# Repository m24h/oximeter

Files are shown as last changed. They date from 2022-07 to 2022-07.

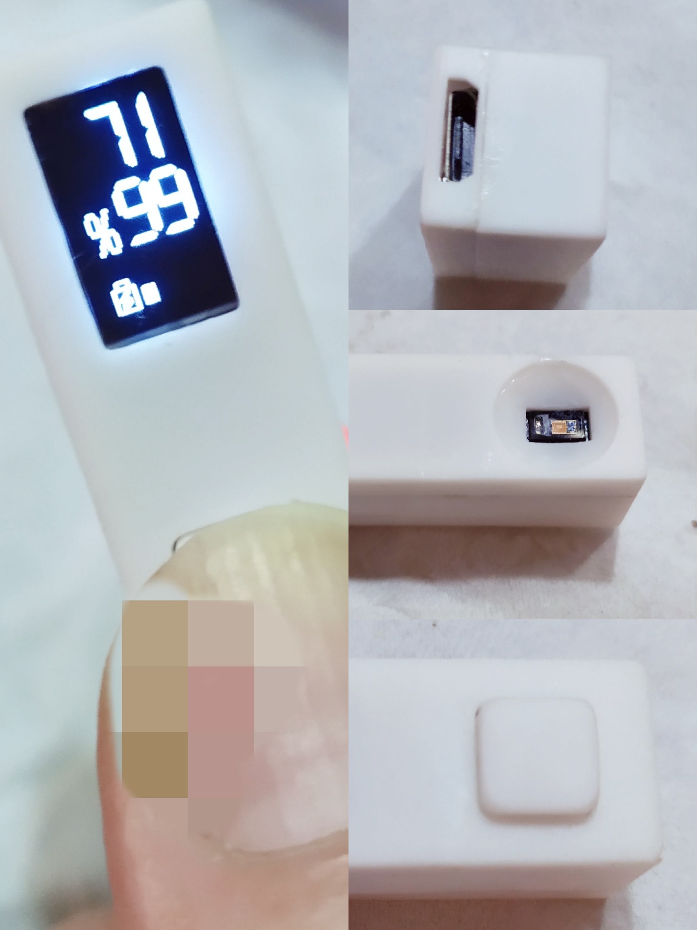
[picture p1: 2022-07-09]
running/usage.jpg

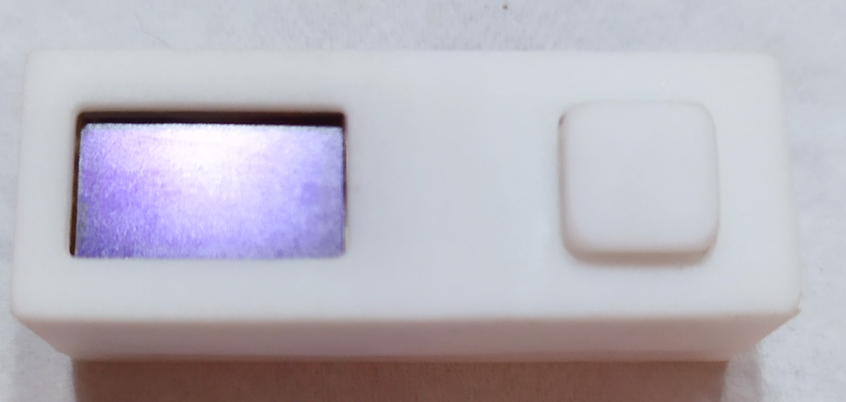
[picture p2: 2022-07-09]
running/top.jpg

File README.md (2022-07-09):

# oximeter
A small oximeter using MAX30102/STC8G1K08A/0.5-inch-OLED/Phase-Detect algorithm

features:

1. SpO2 detection.
2. Heart beat rate detection.
3. With a USB charging interface.
4. Small and cheap.
5. Compatible with Keil C51 or SDCC

!!!IMPORTANT!!!

First thing:
I made an ergonomic mistake in my design, my original idea was to use a button to turn on the power and the sensor underneath would just fit the finger.
But the excessive pressure affected the blood flowing in the finger, also the results.
I suggest that subsequent developers can modify the PCB and box case, use a toggle switche instead of the button, which can be placed on the side of the case, and place the sensor on the same side of the OLED (Top side), So the users can just touch the sensor surface gently by a finger, that would result in fast and accurate detection results.

Second thing:
Hex file for burning/Downloading is included here, TTL serial port is connected to D+/D- pin of USB charging interface, subsequent developers can also try to download hex file directly using pseudo USB downloading port of STC8G1K08A (ID pin of micro-USB port is required to be connected to GND, but I've never tried, and I heard that there is a certain failure rate).
But STC-ISP V6.90 (the STC official downloading software) has an strange BUG, which will cause straightforward downloading to fail.
In my design, I put const parameters like fonts and some tables into EEPROM area (which is indexed from 0x2000), STC-ISP says "This file is over the valid scope, and the exceeding part has been moved to EEPROM area", which looks as expected, BUT it is not. STC-ISP does not split the hex file at 0x2000, but at 0x1FF9.
The workaround for this strange problem is to manually delete first 7 bytes at "EEPROM Buffer" tab-page on the STC-ISP interface, and "Save Buffer" to a .bin file, and re-load the file using "Open EEPROM file", the burn it.

Other downloading things:
IRC frequency is 22.1184MHz.
Don't enable WDT.
Rest pin is used as I/O port.

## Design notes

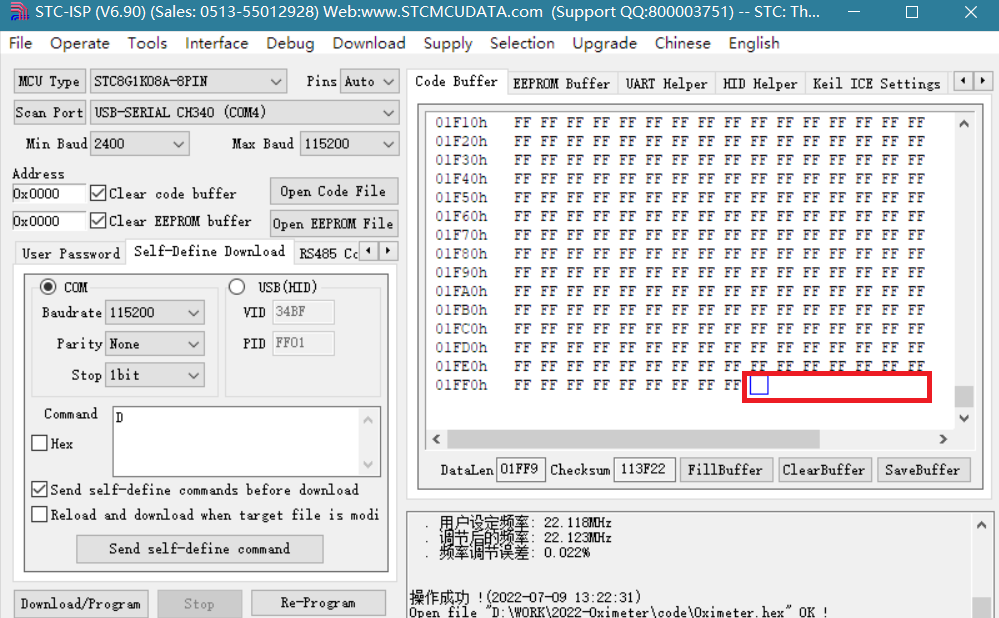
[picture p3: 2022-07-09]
running/stc-isp-wrong-splitting.png

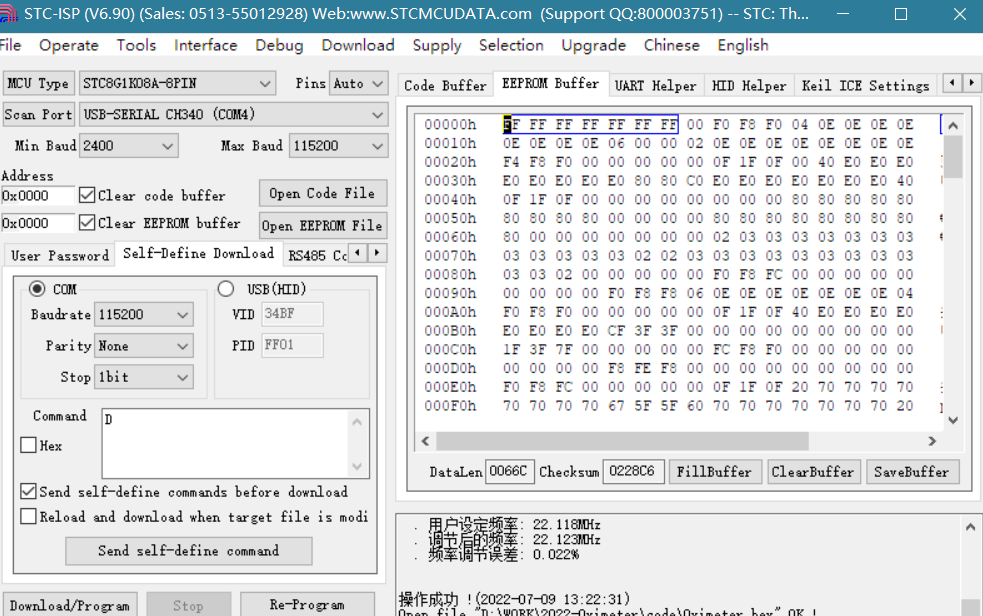
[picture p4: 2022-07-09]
running/stc-isp-must-delete-7bytes.png

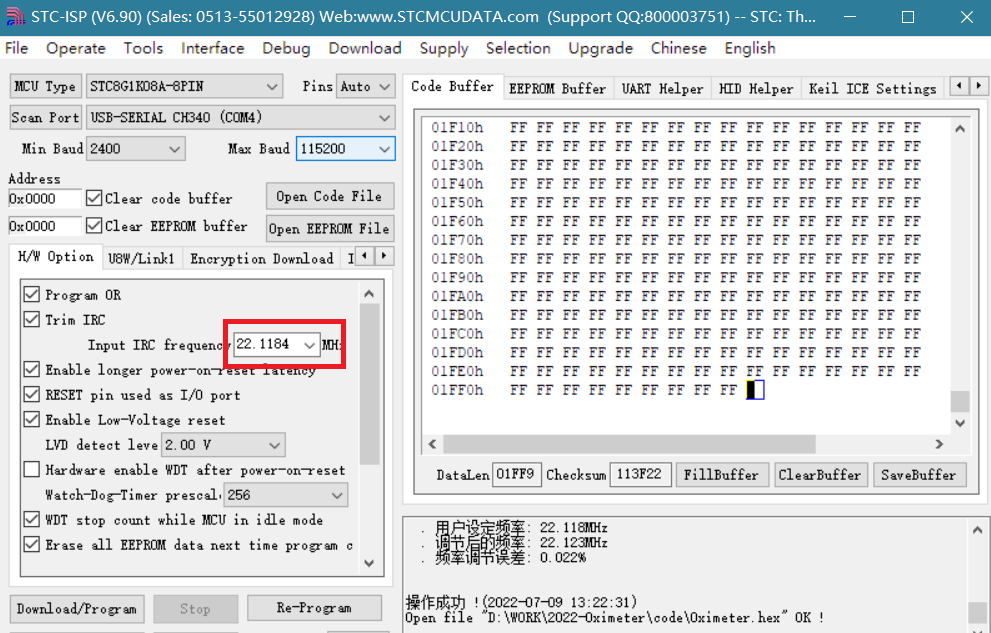
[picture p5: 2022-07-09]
running/stc-isp-freq.png

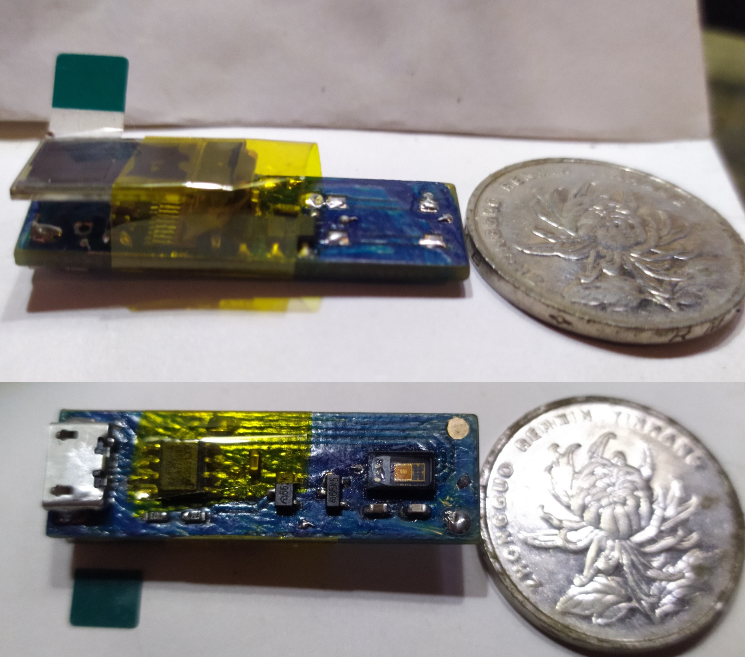
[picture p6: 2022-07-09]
running/pcb.jpg

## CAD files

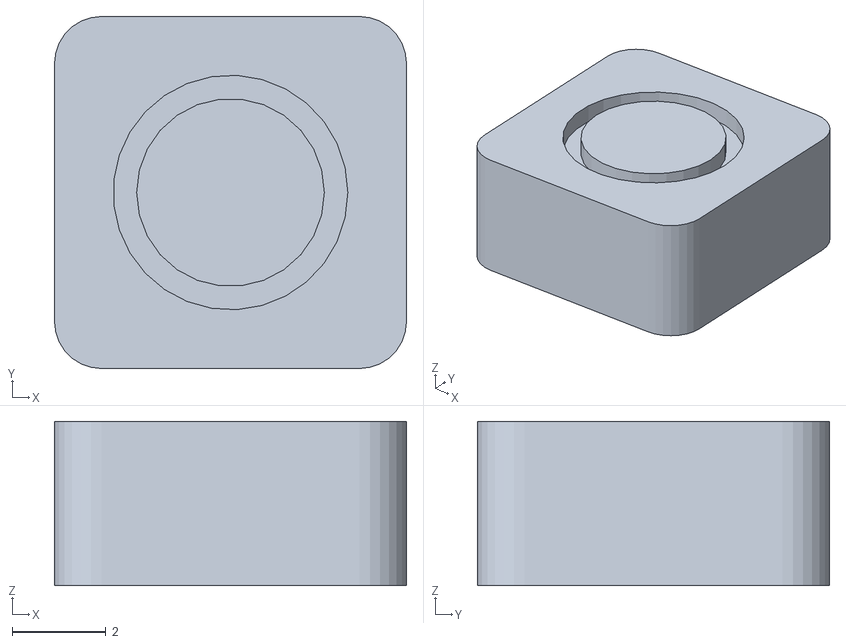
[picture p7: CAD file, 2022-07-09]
parts/button.stl
7.50 x 7.50 x 3.50

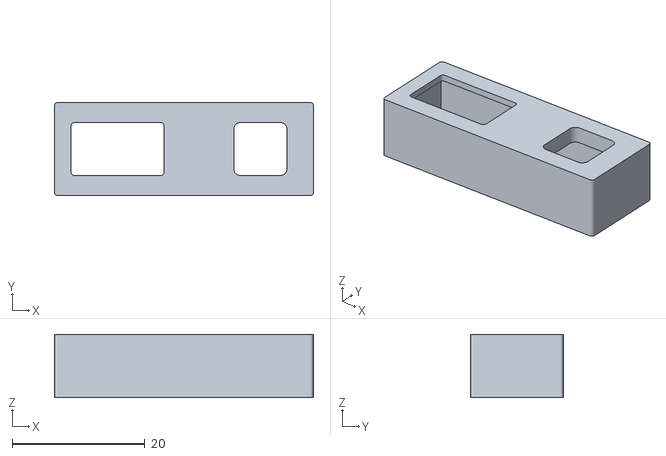
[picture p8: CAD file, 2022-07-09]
parts/top.stl
39.0 x 14.0 x 9.50

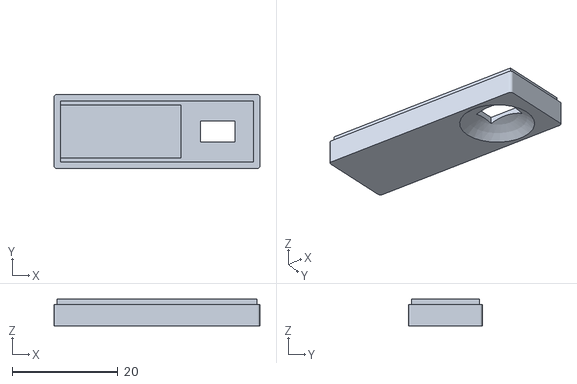
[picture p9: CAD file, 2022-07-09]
parts/bottom.stl
39.0 x 14.0 x 5.10

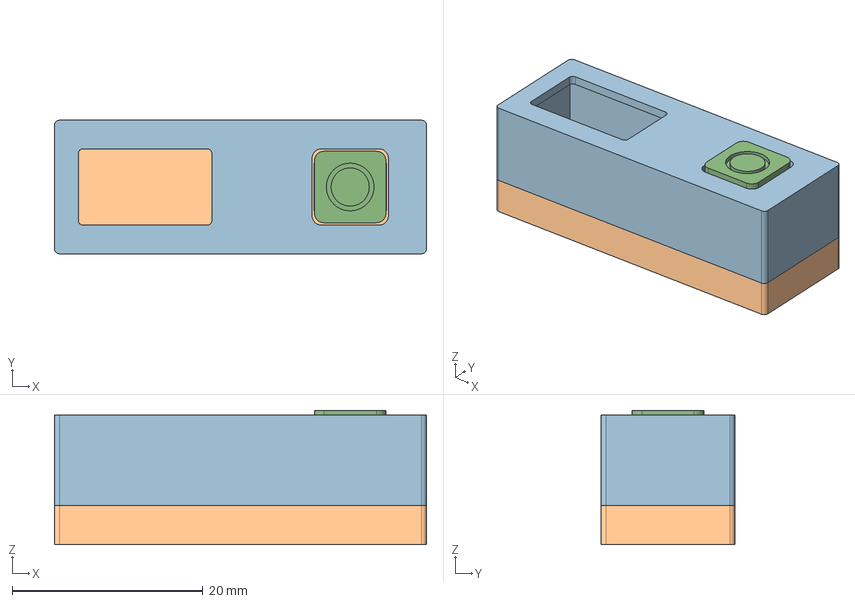
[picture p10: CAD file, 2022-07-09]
parts/box.FCStd
39.0 x 14.0 x 14.1 mm
top
button
bottom

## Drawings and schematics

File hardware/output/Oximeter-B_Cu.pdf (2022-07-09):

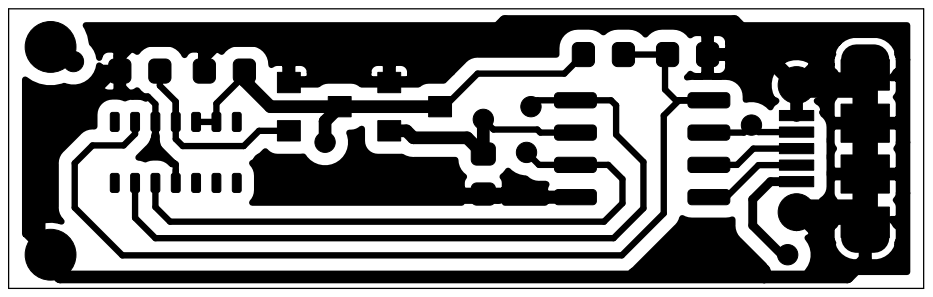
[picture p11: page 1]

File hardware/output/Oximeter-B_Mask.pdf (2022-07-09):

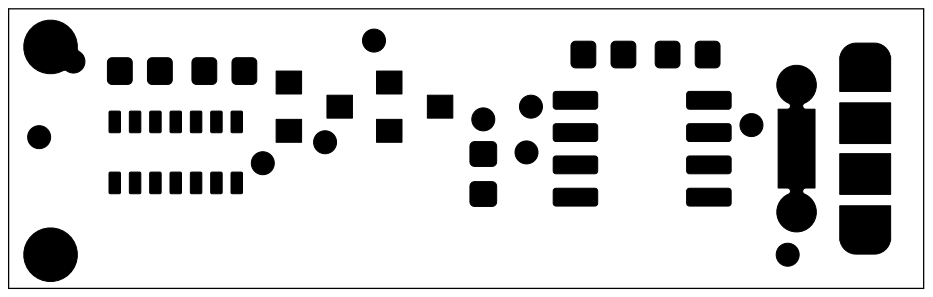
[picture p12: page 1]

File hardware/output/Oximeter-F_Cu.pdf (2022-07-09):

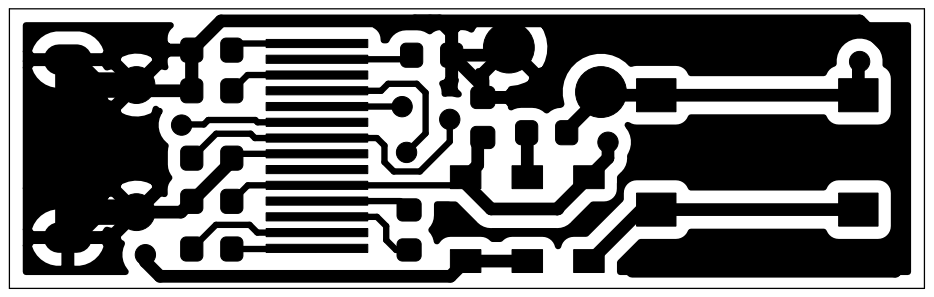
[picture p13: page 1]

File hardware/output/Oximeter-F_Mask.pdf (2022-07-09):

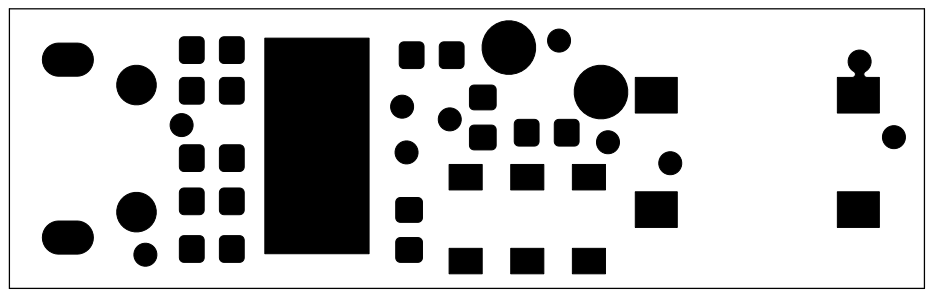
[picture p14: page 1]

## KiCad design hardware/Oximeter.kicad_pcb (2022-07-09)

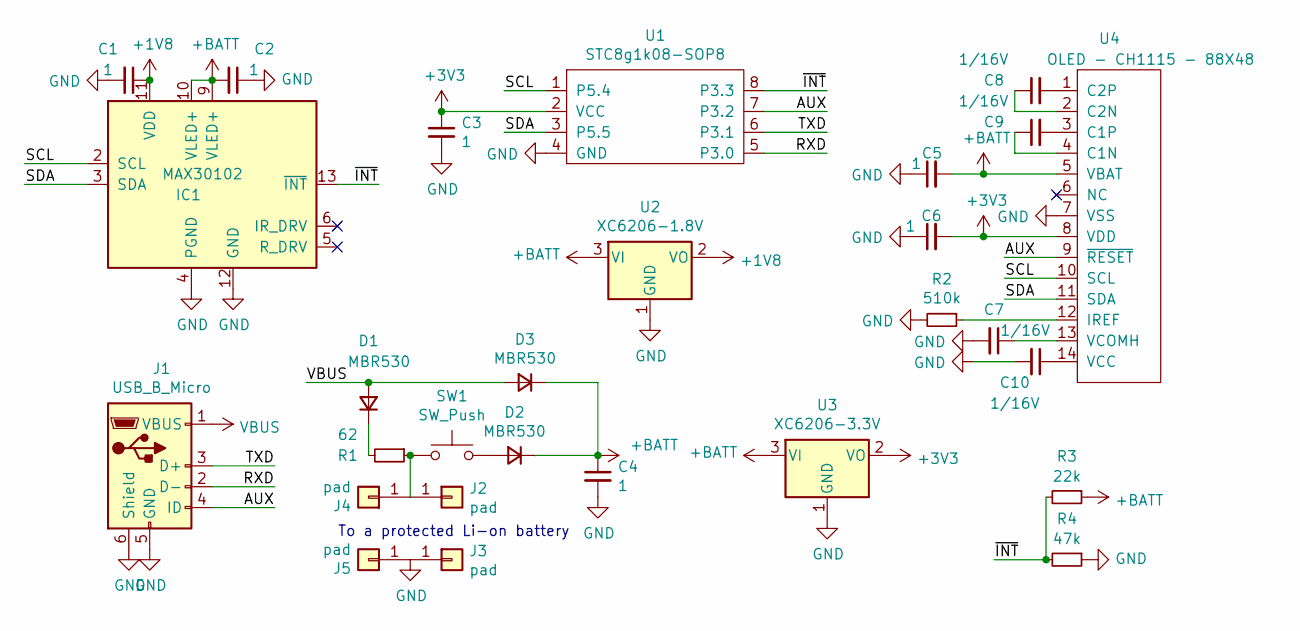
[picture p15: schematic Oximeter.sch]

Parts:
C1, C2, C3, C4, C5, C6: 1; C_0603_1608Metric
C7, C8, C9, C10: 1/16V; C_0603_1608Metric
D1, D2, D3: MBR530; D_SOD-123
IC1: MAX30102; Maxim_OLGA-14_3.3x5.6mm_P0.8mm
J1: USB_B_Micro; USB_Micro-B_Molex-105017-0001
J2, J3, J4, J5: pad; Pad-SMD
R1: 62; R_0603_1608Metric
R2: 510k; R_0603_1608Metric
R3: 22k; R_0603_1608Metric
R4: 47k; R_0603_1608Metric
SW1: SW_Push; SW_Push_1P1T_NO_6x6mm_H9.5mm
U1: STC8g1k08-SOP8; SOP-8_3.9x4.9mm_P1.27mm
U2: XC6206-1.8V; SOT-23
U3: XC6206-3.3V; SOT-23
U4: OLED - CH1115 - 88X48; OLED-0.5IN-14PIN

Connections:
+1V8: C1.1, IC1.11 (VDD), U2.2 (VO)
+3V3: C3.1, C6.2, U1.2 (VCC), U3.2 (VO), U4.8 (VDD)
+BATT: C2.2, C4.1, C5.2, D2.1 (K), D3.1 (K), IC1.9 (VLED+), IC1.10 (VLED+), R3.1, U2.3 (VI), U3.3 (VI), U4.5 (VBAT)
/AUX: J1.4 (ID), U1.7 (P3.2), U4.9 (~RESET)
/RXD: J1.2 (D-), U1.5 (P3.0)
/SCL: IC1.2 (SCL), U1.1 (P5.4), U4.10 (SCL)
/SDA: IC1.3 (SDA), U1.3 (P5.5), U4.11 (SDA)
/TXD: J1.3 (D+), U1.6 (P3.1)
/~INT: IC1.13 (~INT), R3.2, R4.2, U1.8 (P3.3)
GND: C1.2, C2.1, C3.2, C4.2, C5.1, C6.1, C7.2, C10.2, IC1.4 (PGND), IC1.12 (GND), J1.5 (GND), J1.6 (Shield), J3.1, J5.1, R2.2, R4.1, U1.4 (GND), U2.1 (GND), U3.1 (GND), U4.7 (VSS)
unnamed: C7.1, U4.13 (VCOMH)
unnamed: C8.1, U4.2 (C2N)
unnamed: C8.2, U4.1 (C2P)
unnamed: C9.1, U4.4 (C1N)
unnamed: C9.2, U4.3 (C1P)
unnamed: C10.1, U4.14 (VCC)
unnamed: D1.1 (K), R1.2
unnamed: D2.2 (A), SW1.2
unnamed: J2.1, J4.1, R1.1, SW1.1
unnamed: R2.1, U4.12 (IREF)
VBUS: D1.2 (A), D3.2 (A), J1.1 (VBUS)

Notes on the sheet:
To a protected Li-on battery

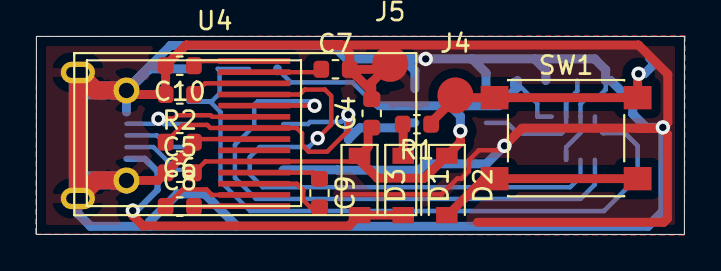
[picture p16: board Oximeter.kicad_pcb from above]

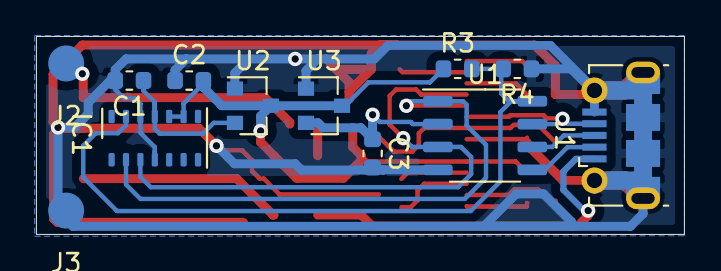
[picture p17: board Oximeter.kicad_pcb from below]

Board: 2 copper layers, 36.0 x 11.0 mm, 28 parts (12 on the bottom side), 21 nets.

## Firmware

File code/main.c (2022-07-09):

#include	"def.h"

#define USE_COS

//#define SER_RAW
//#define SER_FIL
//#define SER_PEAK
//#define SER_HBEAT
#define SER_OUT
//#define SER_SPECTRUM


#define FOSC 22118400UL
#define BGV  1190U
#define BAUDRATE 115200U

// oled flushed every 32 timer events (planned, but maybe delayed if busy)
#define TIMER_FREQ 64

#define IIC_FREQ    200000UL
#define IIC_ADDR_SEN    0xAE
#define IIC_ADDR_OLED   0x78
#define OLED_NOP 0xE3

#define HR_MIN 30
#define HR_MAX 200
#define O2_MIN 10
#define O2_MAX 99
#define BATT_MIN 3300
#define BATT_MAX 4200

#define SEN_BUFFSIZE 32

#define PROX_PA   16
#define PROX_TH   10
#define CALI_AIM  100000UL

// (65536*HR_MIN/60/SEN_RATE-6)=322, -6 is a fixed value for smallest error in whole heart beat rate scope 
#define PD_TADD  322
// (65536/(60*SEN_RATE))=11
#define PD_FADD  11

#define ST_START  0
#define ST_PROX   10
#define ST_PROX1  11
#define ST_CALI   20
#define ST_CALI1  21
#define ST_CALI2  22
#define ST_FIL    30
#define ST_FIL1   31
#define ST_FIL2   32
#define ST_WORK   50
#define ST_WORK1  51
#define ST_STABLE 80

u8  idata g_state=0;   // state defined as ST_ macro 
u8  idata g_staux=0;   // for state-machine sub-state

u32 idata g_timer=0;   // a counter, added 1 every 1/64s
u32 idata g_samps;     // how many samples processed
u32 idata g_lost;      // how many samples losted

i16 idata g_batt=0;    // battery voltage, in mV
i16 idata g_hr;        // heart beat rate per minute, fixed point, need to ">>6"
i16 idata g_o2;        // SpO2 percent, fixed point, need to ">>6"

u8  idata g_red_pa;    // sensor RED LED current 0~0xff:0~50mA
u8  idata g_ir_pa;     // sensor IR LED current 0~0xff:0~50mA
u32 idata g_cali_aim;  // aim of calibrating LED current

i32 idata g_red_dc;    // RED sample DC value 
i16 idata g_red_max;   // RED sample MAX value 
i16 idata g_red_min;   // RED sample MIN value
i32 idata g_ir_dc;     // IR sample DC value 
i16 idata g_ir_max;    // IR sample MAX value 
i16 idata g_ir_min;    // IR sample MIN value

u8  xdata g_buff[SEN_BUFFSIZE*6];
i16 xdata g_hr_i[HR_MAX-HR_MIN+1];
i16 xdata g_hr_q[HR_MAX-HR_MIN+1];

u8 code CHAR_DIGI [][64]={{  // every character is 16 COMs ( 2 pages) x 32 COLs
	0x00,0xF0,0xF8,0xF0,0x04,0x0E,0x0E,0x0E,0x0E,0x0E,0x0E,0x0E,0x0E,0x06,0x00,0x00,
	0x02,0x0E,0x0E,0x0E,0x0E,0x0E,0x0E,0x0E,0x0E,0xF4,0xF8,0xF0,0x00,0x00,0x00,0x00,
	0x00,0x0F,0x1F,0x0F,0x00,0x40,0xE0,0xE0,0xE0,0xE0,0xE0,0xE0,0xE0,0xE0,0x80,0x80,
	0xC0,0xE0,0xE0,0xE0,0xE0,0xE0,0xE0,0xE0,0x40,0x0F,0x1F,0x0F,0x00,0x00,0x00,0x00,/*"0",0*/ 
	},{
	0x00,0x00,0x00,0x00,0x80,0x80,0x80,0x80,0x80,0x80,0x80,0x80,0x80,0x00,0x00,0x00,
	0x00,0x80,0x80,0x80,0x80,0x80,0x80,0x80,0x80,0x80,0x00,0x00,0x00,0x00,0x00,0x00,
	0x00,0x02,0x03,0x03,0x03,0x03,0x03,0x03,0x03,0x03,0x03,0x03,0x03,0x03,0x02,0x02,
	0x03,0x03,0x03,0x03,0x03,0x03,0x03,0x03,0x03,0x03,0x03,0x02,0x00,0x00,0x00,0x00,/*"1",1*/
	},{
	0x00,0xF0,0xF8,0xFC,0x00,0x00,0x00,0x00,0x00,0x00,0x00,0x00,0x00,0xF0,0xF8,0xF8,
	0x06,0x0E,0x0E,0x0E,0x0E,0x0E,0x0E,0x0E,0x04,0xF0,0xF8,0xF0,0x00,0x00,0x00,0x00,
	0x00,0x0F,0x1F,0x0F,0x40,0xE0,0xE0,0xE0,0xE0,0xE0,0xE0,0xE0,0xE0,0xCF,0x3F,0x3F,
	0x00,0x00,0x00,0x00,0x00,0x00,0x00,0x00,0x00,0x1F,0x3F,0x7F,0x00,0x00,0x00,0x00,/*"2",2*/
	},{
	0x00,0xFC,0xF8,0xF0,0x00,0x00,0x00,0x00,0x00,0x00,0x00,0x00,0x00,0xF8,0xFE,0xF8,
	0x00,0x00,0x00,0x00,0x00,0x00,0x00,0x00,0x00,0xF0,0xF8,0xFC,0x00,0x00,0x00,0x00,
	0x00,0x0F,0x1F,0x0F,0x20,0x70,0x70,0x70,0x70,0x70,0x70,0x70,0x70,0x67,0x5F,0x5F,
	0x60,0x70,0x70,0x70,0x70,0x70,0x70,0x70,0x20,0x0F,0x1F,0x0F,0x00,0x00,0x00,0x00,/*"3",3*/
	},{
	0x00,0x00,0x00,0x02,0x06,0x0E,0x0E,0x0E,0x0E,0x0E,0x0E,0x0E,0x0E,0xE6,0xF8,0xF8,
	0x00,0x00,0x00,0x00,0x00,0x00,0x00,0x00,0x00,0x00,0x00,0x00,0x00,0x00,0x00,0x00,
	0x00,0x80,0xC0,0xC0,0xE0,0xE0,0xE0,0xE0,0xE0,0xE0,0xE0,0xE0,0xE0,0xCF,0xBF,0xBF,
	0xC0,0xE0,0xE0,0xE0,0xE0,0xE0,0xE0,0xE0,0xE0,0xE0,0xC0,0x80,0x00,0x00,0x00,0x00,/*"4",4*/
	},{
	0x00,0xF0,0xF8,0xF0,0x04,0x0E,0x0E,0x0E,0x0E,0x0E,0x0E,0x0E,0x0E,0xE6,0xF8,0xF8,
	0x00,0x00,0x00,0x00,0x00,0x00,0x00,0x00,0x00,0xF8,0xFC,0xFE,0x00,0x00,0x00,0x00,
	0x00,0x7F,0x3F,0x0F,0x00,0x00,0x00,0x00,0x00,0x00,0x00,0x00,0x00,0x1F,0x3F,0x3F,
	0xC0,0xE0,0xE0,0xE0,0xE0,0xE0,0xE0,0xE0,0x40,0x0F,0x1F,0x0F,0x00,0x00,0x00,0x00,/*"5",5*/
	},{
	0x00,0xF0,0xF8,0xF0,0x04,0x0E,0x0E,0x0E,0x0E,0x0E,0x0E,0x0E,0x0E,0xE6,0xFA,0xFA,
	0x06,0x0E,0x0E,0x0E,0x0E,0x0E,0x0E,0x0E,0x0E,0xF4,0xF8,0xF0,0x00,0x00,0x00,0x00,
	0x00,0x7F,0x3F,0x0F,0x00,0x00,0x00,0x00,0x00,0x00,0x00,0x00,0x00,0x1F,0x3F,0x3F,
	0xC0,0xE0,0xE0,0xE0,0xE0,0xE0,0xE0,0xE0,0x40,0x0F,0x1F,0x0F,0x00,0x00,0x00,0x00,/*"6",6*/
	},{
	0x00,0xFE,0xFC,0xF8,0x00,0x00,0x00,0x00,0x00,0x00,0x00,0x00,0x00,0x00,0x00,0x00,
	0x00,0x00,0x00,0x00,0x00,0x00,0x00,0x00,0x00,0x00,0x00,0x00,0x00,0x00,0x00,0x00,
	0x00,0x3F,0x1F,0x2F,0x30,0x38,0x38,0x38,0x38,0x38,0x38,0x38,0x38,0x30,0x20,0x20,
	0x30,0x38,0x38,0x38,0x38,0x38,0x38,0x38,0x38,0x38,0x30,0x20,0x00,0x00,0x00,0x00,/*"7",7*/
	},{
	0x00,0xF0,0xF8,0xF0,0x04,0x0E,0x0E,0x0E,0x0E,0x0E,0x0E,0x0E,0x0E,0xE6,0xF8,0xF8,
	0x06,0x0E,0x0E,0x0E,0x0E,0x0E,0x0E,0x0E,0x0E,0xF4,0xF8,0xF0,0x00,0x00,0x00,0x00,
	0x00,0x0F,0x1F,0x0F,0x40,0xE0,0xE0,0xE0,0xE0,0xE0,0xE0,0xE0,0xE0,0xCF,0xBF,0xBF,
	0xC0,0xE0,0xE0,0xE0,0xE0,0xE0,0xE0,0xE0,0x40,0x0F,0x1F,0x0F,0x00,0x00,0x00,0x00,/*"8",8*/
	},{
	0x00,0xF0,0xF8,0xF0,0x04,0x0E,0x0E,0x0E,0x0E,0x0E,0x0E,0x0E,0x0E,0xE6,0xF8,0xF8,
	0x00,0x00,0x00,0x00,0x00,0x00,0x00,0x00,0x00,0xF0,0xF8,0xFC,0x00,0x00,0x00,0x00,
	0x00,0x0F,0x1F,0x0F,0x40,0xE0,0xE0,0xE0,0xE0,0xE0,0xE0,0xE0,0xE0,0xCF,0xBF,0xBF,
	0xC0,0xE0,0xE0,0xE0,0xE0,0xE0,0xE0,0xE0,0x40,0x0F,0x1F,0x0F,0x00,0x00,0x00,0x00,/*"9",9*/
}};

u8 code CHAR_NA [64] = {
	0x00,0x00,0x00,0x00,0x00,0x00,0x00,0x00,0x00,0x00,0x00,0x00,0x00,0x00,0x00,0x00,
	0x00,0x00,0xF8,0xFC,0xFE,0x00,0x00,0x00,0x00,0x00,0x00,0x00,0x00,0x00,0x00,0x00,
	0x00,0x00,0x00,0x00,0x00,0x00,0x00,0x00,0x00,0x00,0x00,0x00,0x00,0x00,0x00,0x00,
	0x00,0x00,0x07,0x07,0x03,0x00,0x00,0x00,0x00,0x00,0x00,0x00,0x00,0x00,0x00,0x00,/*"-"*/
};

u8 code CHAR_SP [64] = {
	0x00,0x00,0x00,0x00,0x00,0x00,0x00,0x00,0x00,0x00,0x00,0x00,0x00,0x00,0x00,0x00,
	0x00,0x00,0x00,0x00,0x00,0x00,0x00,0x00,0x00,0x00,0x00,0x00,0x00,0x00,0x00,0x00,
	0x00,0x00,0x00,0x00,0x00,0x00,0x00,0x00,0x00,0x00,0x00,0x00,0x00,0x00,0x00,0x00,
	0x00,0x00,0x00,0x00,0x00,0x00,0x00,0x00,0x00,0x00,0x00,0x00,0x00,0x00,0x00,0x00,/*" "*/
};

u8 code CHAR_PCT [64] = {
	0x00,0x00,0x00,0x00,0x00,0x00,0x00,0x00,0x00,0x00,0x38,0x28,0x44,0x44,0x44,0x44,
	0x44,0x44,0x28,0xB8,0x80,0x80,0x40,0x40,0x60,0x20,0x20,0x30,0x10,0x00,0x00,0x00,
	0x00,0x00,0x00,0x00,0x00,0x00,0x00,0x00,0x00,0x00,0x0C,0x04,0x04,0x06,0x02,0x02,
	0x03,0x01,0x01,0x0E,0x0A,0x11,0x11,0x11,0x11,0x11,0x11,0x0A,0x0E,0x00,0x00,0x00,/*"%"*/
};

u8 code CHAR_BATT [32] = {
	0x00,0xE0,0x20,0x20,0xF8,0x08,0x08,0x88,0xC8,0xE8,0x88,0xC8,0xC8,0x48,0xF8,0x00,
	0x00,0x07,0x04,0x04,0x1F,0x12,0x13,0x11,0x10,0x13,0x13,0x11,0x10,0x10,0x1F,0x00,/*"batt.bmp"*/
};

u8 code BATT_VOLT [9] = {
  0x00,0x01,0x03,0x07,0x07,0x17,0x37,0x77,0x77,
};

u8 code CHAR_NUM [] = {
	'0','1','2','3','4','5','6','7','8','9','A','B','C','D','E','F'
};

// SpO2 table, multiplied by 64
i16 code O2_LUT [] = {
  6397,	6397,	6397,	6397,	6397,	6397,	6397,	6397,	6397,	6397,	6397,	6397,
	6397,	6397,	6397,	6397,	6397,	6397,	6397,	6397,	6397,	6397,	6397,	6396,	
	6393,	6389,	6383,	6376,	6368,	6358,	6347,	6334,	6320,	6305,	6288,	6270,
	6250,	6229,	6207,	6183,	6158,	6131,	6103,	6073,	6043,	6010,	5977,	
	5941,	5905,	5867,	5828,	5787,	5745,	5701,	5656,	5610,	5562,	5513,	
	5462,	5410,	5357,	5302,	5246,	5188,	5129,	5068,	5007,	4943,	4879,
	4812,	4745,	4676,	4606,	4534,	4461,	4386,	4310,	4233,	4154,	4074,	
	3992,	3909,	3825,	3739,	3652,	3563,	3473,	3382,	3289,	3195,	3099,
	3002,	2903,	2804,	2702,	2600,	2495,	2390,	2283,	2175,	2065,	1954,
	1841,	1727,	1612,	1495,	1377,	1257,	1136,	1014,	890,	765,	638,
	510,	380,	250,	117,	0
};

#ifdef USE_COS

i16 code COS_LUT [] = {
	256,	256,	256,	255,	255,	254,	253,	252,	251,	250,	248,	247,	245,	243,	241,	239,
	237,	234,	231,	229,	226,	223,	220,	216,	213,	209,	206,	202,	198,	194,	190,	185,
	181,	177,	172,	167,	162,	157,	152,	147,	142,	137,	132,	126,	121,	115,	109,	104,
	98,	92,	86,	80,	74,	68,	62,	56,	50,	44,	38,	31,	25,	19,	13,	6,	
	0,	-6,	-13,	-19,	-25,	-31,	-38,	-44,	-50,	-56,	-62,	-68,	-74,	-80,	-86,	-92,
	-98,	-104,	-109,	-115,	-121,	-126,	-132,	-137,	-142,	-147,	-152,	-157,	-162,	-167,	-172,	-177,
	-181,	-185,	-190,	-194,	-198,	-202,	-206,	-209,	-213,	-216,	-220,	-223,	-226,	-229,	-231,	-234,	
	-237,	-239,	-241,	-243,	-245,	-247,	-248,	-250,	-251,	-252,	-253,	-254,	-255,	-255,	-256,	-256,
	-256,	-256,	-256,	-255,	-255,	-254,	-253,	-252,	-251,	-250,	-248,	-247,	-245,	-243,	-241,	-239,
	-237,	-234,	-231,	-229,	-226,	-223,	-220,	-216,	-213,	-209,	-206,	-202,	-198,	-194,	-190,	-185,
	-181,	-177,	-172,	-167,	-162,	-157,	-152,	-147,	-142,	-137,	-132,	-126,	-121,	-115,	-109,	-104,
	-98,	-92,	-86,	-80,	-74,	-68,	-62,	-56,	-50,	-44,	-38,	-31,	-25,	-19,	-13,	-6,	
	0,	6,	13,	19,	25,	31,	38,	44,	50,	56,	62,	68,	74,	80,	86,	92,	
	98,	104,	109,	115,	121,	126,	132,	137,	142,	147,	152,	157,	162,	167,	172,	177,
	181,	185,	190,	194,	198,	202,	206,	209,	213,	216,	220,	223,	226,	229,	231,	234,
	237,	239,	241,	243,	245,	247,	248,	250,	251,	252,	253,	254,	255,	255,	256,	256
};
	
#endif

// delay in millisecond, specified by "ms"
void delay_ms(u16 ms)
{
	u8 i;
	u8 j;
	
	while (ms--){
  	i = 1+((u16)(FOSC/3000UL)>>8); 
  	j = (u8)(FOSC/3000UL);
		do {
			while (--j);
		} while (--i);		
	}		
}


void ser_send(u8 ch)
{
	SBUF=ch;
	while (!TI);
	TI=0;
}

void ser_u8 (u8 u)
{
	ser_send(CHAR_NUM[u>>4]);
	ser_send(CHAR_NUM[u&0x0f]);
}

void ser_u16 (u16 u)
{
	ser_u8(((u16s*)&u)->h);
	ser_u8(((u16s*)&u)->l);
}

void ser_u32 (u32 u)
{
	ser_u8(((u32s*)&u)->hh);
	ser_u8(((u32s*)&u)->hl);
	ser_u8(((u32s*)&u)->lh);
	ser_u8(((u32s*)&u)->ll);
}

// read ADC ch, ch==0x0f means internal Gap-Band voltage, output 0~1023
u16 adc_read(u8 ch)
{
	  ADC_CONTR = 0xC0 | (ch & 0x0f); // power on, start, select internal Gap-Band channel
    _nop_();
    _nop_();
    while (!(ADC_CONTR & 0x20));   // wait completing
    ADC_CONTR = 0x8f;  // power on, stop, select internal Gap-Band channel 

  	return ((u16)ADC_RES << 8) | (u16)ADC_RESL; 
}

// get voltage of battery
void batt_get ()
{
	u16 t;
	u16 gb;
	
	if (!P33) return; // pulled down by intr.
	t=adc_read(0x03); // read P3.3(ADC3)
	if (!P33) return; // pulled down by intr.
			
  gb=adc_read(0x0f); // read internal Gap-Band voltage
	if (gb<32) return; // avoid fault
	
  t=(i16)(69UL*BGV*t/gb/47L);

	if (g_batt>2000) {
		g_batt += ((i16)t - g_batt)>>4; // T(0.63)=16 sample points
	}	else
		g_batt = t; 
}

void iic_wait() {
	while (!(I2CMSST & 0x40)); 
	I2CMSST &= ~0x40;
}

void iic_stop()
{
	I2CMSCR = 0x06;
	iic_wait();
}

void iic_start(u8 dev)
{
	I2CTXD = dev;                               
	I2CMSCR = 0x09;                            
	iic_wait();
}

void iic_send(u8 dat)
{
	I2CTXD = dat;                               
	I2CMSCR = 0x0A;                            
	iic_wait();
}

u8 iic_recv_ack()
{
	I2CMSCR = 0x0B;                             
	iic_wait();
	return I2CRXD;
}

u8 iic_recv_nak()
{
	I2CMSCR = 0x0C;                             
	iic_wait();
	return I2CRXD;
}

// get 1 byte from dev
u8 sen_get(u8 addr)
{
	u8 ret;

	iic_start(IIC_ADDR_SEN & 0xfe);
	iic_send(addr);
	iic_start(IIC_ADDR_SEN | 0x01);
	ret=iic_recv_nak();
	iic_stop();
	
	return ret;
}

// write a byte to sensor
void sen_put(u8 addr, u8 dat) 
{
	iic_start(IIC_ADDR_SEN & 0xfe);
	iic_send(addr);
	iic_send(dat);
	iic_stop();
}

// read bytes from sensor
void sen_read(u8 addr, u8 *p, u8 len)
{
	if (!len) return;
	
	iic_start(IIC_ADDR_SEN & 0xfe);
	iic_send(addr);
	iic_start(IIC_ADDR_SEN | 0x01);
	while (--len) {
		*(p++) = iic_recv_ack();
	}
	*p = iic_recv_nak();
	iic_stop();
}

// set sensor LED/IR current and ADC range
void sen_cali()
{
	sen_put(0x0D, g_red_pa); // RED LED current
	sen_put(0x0C, g_ir_pa);  // IR LED current
}
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
